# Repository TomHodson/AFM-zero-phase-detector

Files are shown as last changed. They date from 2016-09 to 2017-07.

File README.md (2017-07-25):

# AFM-zero-phase-detector
schematics and notes for a quartz resonator based atomic force microscope.

#Files
- sweep.py a utility to send frequency values down the serial line for testing
- AFM_stripboard_schematic schematics for the board that's built up on stripboard
- Arduino_AD9833_serial_controller an arduino sketch to control the frequency generator via the serial line.

#System components

##Frequency generator 

AD9833 arduino code
http://www.vwlowen.co.uk/arduino/AD9833-waveform-generator/AD9833-waveform-generator.htm

ad9833 datasheet
http://www.analog.com/media/en/technical-documentation/data-sheets/AD9833.pdf

AD9833 module with a 25MHz reference clock. It works by setting an ADC from a sine wave lookup table once per clock cycle. Gives reasonably clean waveforms up to about 1MHz.

controlled through SPI interface, pins are CLK and DATA along with a chip select pin called FSYNC that needs to be brought low when sending data and high to tell the chip you’re finished.

SPI mode 2 (data on falling edge of clock), MSB first

the frequency register is 28 bits long, if you set it to x then the generated frequency will be 

output frequency = x * reference frequency / (2^28)

If you read the data sheet you’ll see that you need to send the value 0x2000 to put the IC in sine wave mode. If you read the included Arduino code you’ll see it’s actually sends 0x2003 which has the last two bits set, one that should put it in triangle wave mode and one bit that’s reserved and should always be 0. I cannot explain this but it seems to generate a sine wave, 0x2000 does not.

The sine and triangle wave outputs are around 0.6v pk-pk coming from the module.

The module is currently wired up to an arduino nano. There's variable gain opamp stage that you can control from a potentiometer and another pot wired up to A7 that you can use as input to arduino sketches.

##Phase detector

Measures the phase difference between the signal coming from the frequency generator and the current through the tuning fork AFM. Does zero crossing detection on both signals, using one to start a linear ramp (555) then uses the other to trigger a sample and hold IC, outputs this value. 

sample and hold LF198 data sheet
http://www.ti.com/lit/ds/symlink/lf398-n.pdf

Note: The output of the Sample and hold IC is steady when in hold mode but shows a transient when the IC is sampling, two can be chained to negate this issue. 

Freq Generator —> tuning fork —> preamp —> zero crossing detector —> | Ramp 

Freq Generator —> zero crossing detector —————————————-> |

Signal Ranger (Interface, DACs and ADCs)

+- 10v DAC outputs to drive piezos, ADC inputs to measure phase and amplitude information.

Need some mechanism to control the 

Manufacturer page and manual
http://www.softdb.com/dsp-products-SR-MK2.php
http://www.softdb.com/_files/_dsp_division/SignalRanger_mk2_UsersManual.pdf

Needs firmware.

Driven by GXSM.

##Power supply
https://octopart.com/tmp+15515c-tracopower-8602141

Tracopower TMP 15515C
5V @ 380mA
+- 15V @ +- 150mA

May need to be loaded at 10-20% rated current to get best stability.

V1 negative appears to the 5v ground
V1 positive is 5v
V2 is 15v
V3 is -15v
Com 2/3 is GND for the +-15V rails

The two grounds appear connected and both are connected with a wire in the box to mains earth return.

##Useful links

Initial 0PM-AFM paper
https://drive.google.com/file/d/0B9IbJ1fnFICZQWVrSVRpWlJHZWFQMFR3cmFBQ0w3NExQVEFZ/view

12: describes tuning fork based AFM
http://dx.doi.org/10.1063/1.113340

9: explanation of dissipation’s effect on resonant frequency and phase
http://dx.doi.org/10.1063/1.2355437

15: description of phase detector:
http://dx.doi.org/10.1063/1.1149968

AD9833 arduino code
http://www.vwlowen.co.uk/arduino/AD9833-waveform-generator/AD9833-waveform-generator.htm

ad9833 datasheet
http://www.analog.com/media/en/technical-documentation/data-sheets/AD9833.pdf

sample and hold lf198 data sheet
http://www.ti.com/lit/ds/symlink/lf398-n.pdf

signal ranger page
http://www.softdb.com/dsp-products-SR-MK2.php
http://www.softdb.com/_files/_dsp_division/SignalRanger_mk2_UsersManual.pdf

A paper on the properties of quartz tuning forks
http://laplace.ucv.cl/Cursos/FisicaExperimental_2/Old/AJP000415.pdf

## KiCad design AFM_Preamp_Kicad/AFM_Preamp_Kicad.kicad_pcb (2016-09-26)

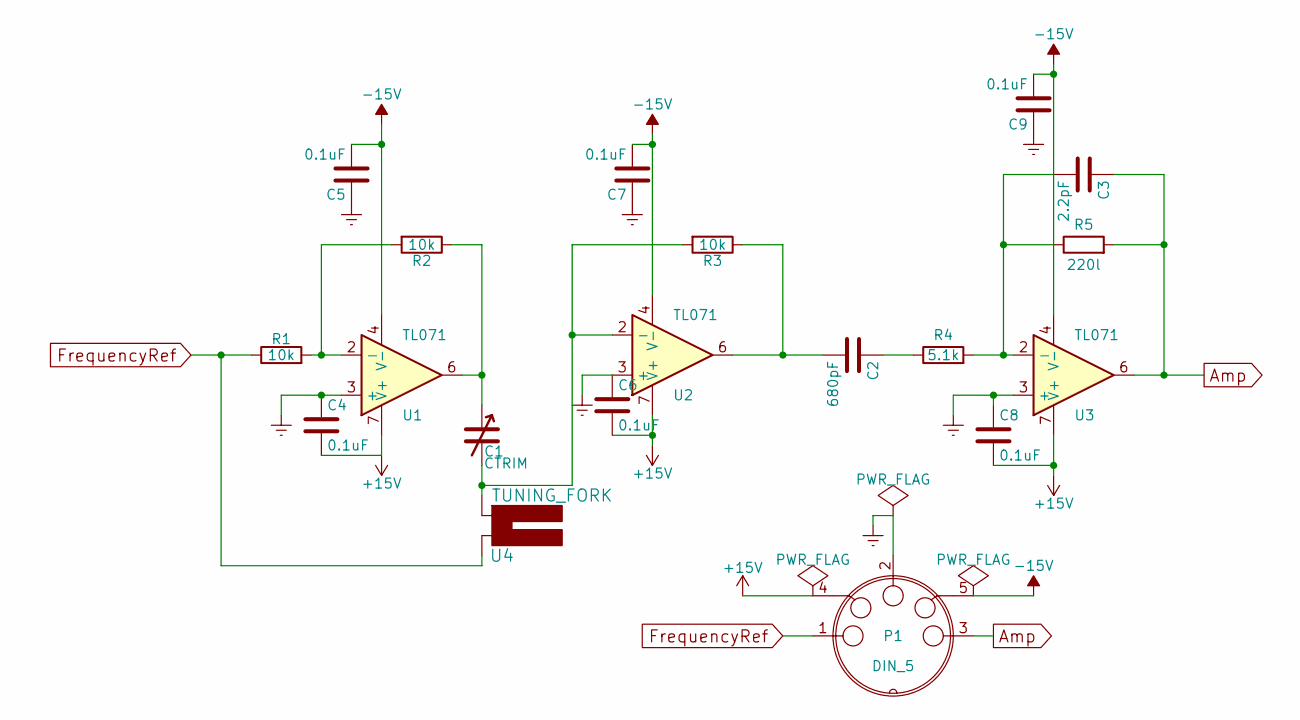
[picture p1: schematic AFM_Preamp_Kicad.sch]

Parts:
C1: CTRIM; C_Radial_D10_L13_P5
C2: 680pF; C_Disc_D3_P2.5
C3: 2.2pF; C_Disc_D3_P2.5
C4, C5, C6, C7, C8, C9: 0.1uF; C_Disc_D3_P2.5
P1: DIN_5; Pin_Header_Straight_1x05
R1, R2, R3: 10k; Resistor_Horizontal_RM10mm
R4: 5.1k; Resistor_Horizontal_RM10mm
R5: 220l; Resistor_Horizontal_RM10mm
U1, U2, U3: TL071; DIP-8_W7.62mm
U4: TUNING_FORK; Pin_Header_Straight_1x02

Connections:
+15V: C4.2, C6.2, C8.2, P1.4, U1.7 (V+), U2.7 (V+), U3.7 (V+)
-15V: C5.2, C7.2, C9.2, P1.5, U1.4 (V-), U2.4 (V-), U3.4 (V-)
Amp: C3.1, P1.3, R5.2, U3.6
Earth: C4.1, C5.1, C6.1, C7.1, C8.1, C9.1, P1.2, U1.3 (+), U2.3 (+), U3.3 (+)
FrequencyRef: P1.1, R1.1, U4.1
unnamed: C1.1, R2.1, U1.6
unnamed: C1.2, R3.2, U2.2 (-), U4.2
unnamed: C2.1, R4.1
unnamed: C2.2, R3.1, U2.6
unnamed: C3.2, R4.2, R5.1, U3.2 (-)
unnamed: R1.2, R2.2, U1.2 (-)

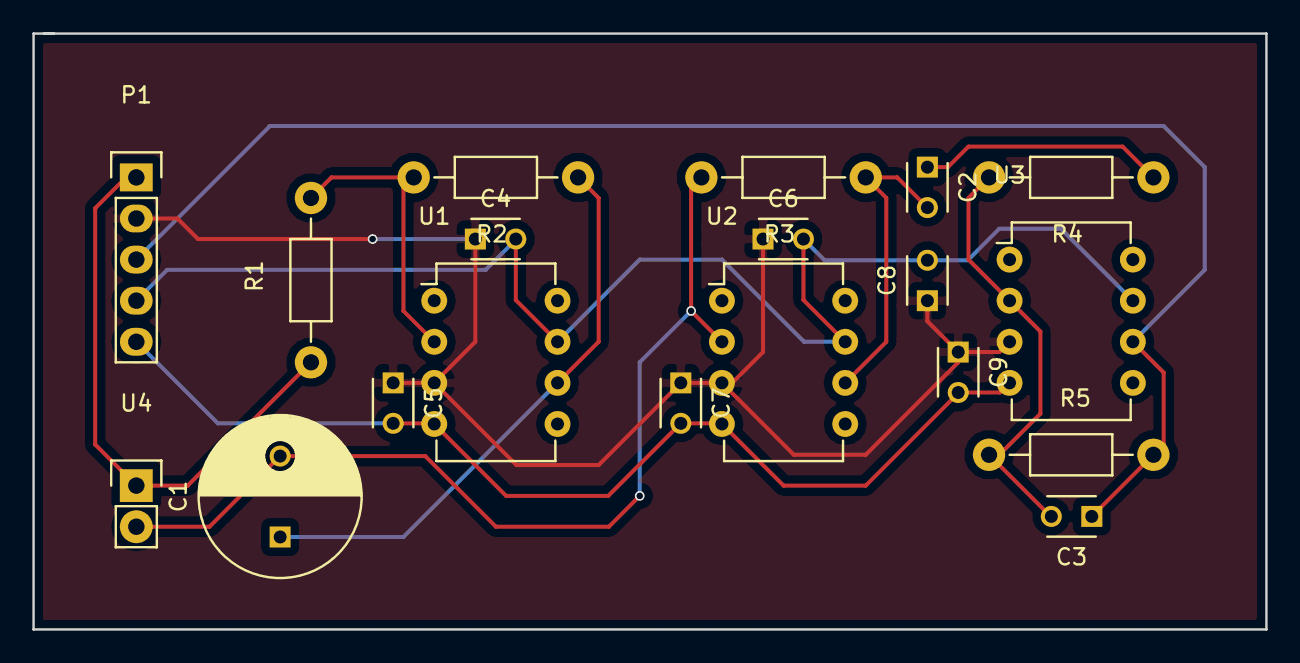
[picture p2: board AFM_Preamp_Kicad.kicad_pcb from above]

Board: 2 copper layers, 76.2 x 36.8 mm, 19 parts (0 on the bottom side), 11 nets.

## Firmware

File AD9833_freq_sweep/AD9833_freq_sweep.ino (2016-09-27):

#include <SPI.h>

const float refFreq = 25000000.0;           // On-board crystal reference frequency
#define SPI_CLOCK_SPEED      12000000

const int SINE = 0x2003;                    // Define AD9833's waveform register value.
const int SQUARE = 0x2020;                  // When we update the frequency, we need to
const int TRIANGLE = 0x2002;                // define the waveform when we end writing.    

const int FSYNC = 10;                       // Standard SPI pins for the AD9833 waveform generator.
const int CLK = 13;                         // CLK and DATA pins are shared with the TFT display.
const int DATA = 11;

const int POT = A7; // the pin that a potentiometer is connected to.
const int PHASE = A5;
const int AMP = A6;

void setup() {
  Serial.begin(9600);
  Serial.setTimeout(5000);
  
  SPI.begin();
  SPI.setDataMode(SPI_MODE2);  
  delay(50);
  
  pinMode(FSYNC, OUTPUT);

  pinMode(POT, INPUT);
  pinMode(PHASE, INPUT);
  pinMode(AMP, INPUT);
  
  AD9833reset(); 
  delay(1000);

  float start_f = 32740;
  float end_f = 32770;
  int steps = 50;

  for(int i = 0; i < steps; i++) {
    float f = start_f + (float(i)/float(steps)) * (end_f - start_f);
    long FreqWord = (f * pow(2, 28)) / refFreq;
    AD9833setFrequency(f, SINE);
    delay(2000);
    int phase = analogRead(PHASE);
    int amp = analogRead(AMP);
    Serial.print(f); Serial.print(", "); Serial.print(amp); Serial.print(", "); Serial.println(phase);
  }
}

void loop() {
}


// AD9833 documentation advises a 'Reset' on first applying power.
void AD9833reset() {
  SPI.beginTransaction(SPISettings(SPI_CLOCK_SPEED, MSBFIRST, SPI_MODE2));
  SPI.transfer16(0x0100);   // Write '1' to AD9833 Control register bit D8.
  delay(10);
  SPI.endTransaction();
}


// Set the frequency and waveform registers in the AD9833.
void AD9833setFrequency(long frequency, int Waveform) {
  long FreqWord = (frequency * pow(2, 28)) / refFreq;
  AD9833setFrequencyRegister(FreqWord, Waveform);
}

// Set the 28 bit frequency and waveform registers directly.
void AD9833setFrequencyRegister(long FreqWord, int Waveform) {

  int MSB = (int)((FreqWord & 0xFFFC000) >> 14);    //Only lower 14 bits are used for data
  int LSB = (int)(FreqWord & 0x3FFF);
  
  //Set control bits 15 and 14 to 0 and 1, respectively, for frequency register 0
  LSB |= 0x4000;
  MSB |= 0x4000; 
  
  digitalWrite(FSYNC, LOW);           // Set FSYNC low before writing to AD9833 registers
  delayMicroseconds(20);              // Give AD9833 time to get ready to receive data.
  
  SPI.beginTransaction(SPISettings(SPI_CLOCK_SPEED, MSBFIRST, SPI_MODE2));
  SPI.transfer16(0x2100);   
  SPI.transfer16(LSB);                  // Write lower 16 bits to AD9833 registers
  SPI.transfer16(MSB);                  // Write upper 16 bits to AD9833 registers.
  SPI.transfer16(0xC000);               // Phase register
  SPI.transfer16(Waveform);             // Exit & Reset to SINE, SQUARE or TRIANGLE

  digitalWrite(FSYNC, HIGH);          //Write done. Set FSYNC high
  SPI.endTransaction();
}

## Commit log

2016-09-18 add schematics for the preamp board
    [AFM_Preamp_Kicad.kicad_pcb, AFM_Preamp_Kicad.sch, _saved_AFM_Preamp_Kicad.sch]
2016-09-26 add preamp schematic
    [AFM_Preamp_Kicad.kicad_pcb]
2016-09-26 add example arduino sketch
2016-09-26 add schematics for the stripboarded circuit
    [AFM_stripboard_schematic.kicad_pcb, AFM_stripboard_schematic.sch]
2016-09-27 add frequency sweep sketch
    [sweep.csv, sweep2.csv]
